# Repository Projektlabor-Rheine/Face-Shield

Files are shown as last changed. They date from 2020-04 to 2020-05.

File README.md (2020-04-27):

# Projektlabor Rheine face shield

This is the Repository of the face shield developed and produced by the *Projektlabor Rheine*.
Feel free to download and cut theese on your own Laser cutter. <br>
**We would be pleased to be named as authors in case of further use.**
**Please do not use in any commercial applications** <br>
The face shield is not a complete protection against the SARS-CoV-2 virus. However, it reduces the risk of infection. <br>
The system is not certified.

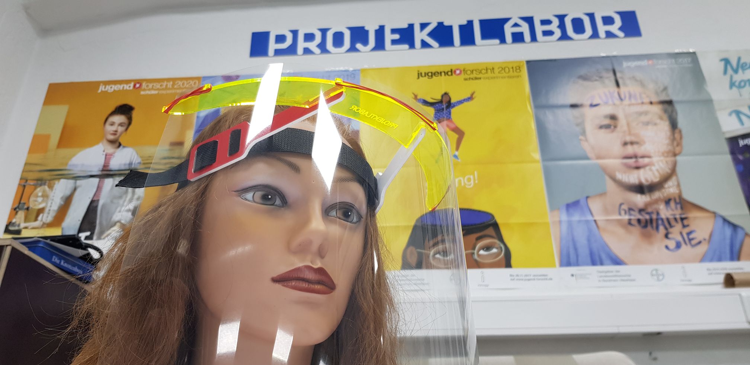
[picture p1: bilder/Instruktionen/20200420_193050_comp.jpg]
Faceshield


## Interested?
**Write to sommer@pkr-projekt.de**

## Ideas?
### Post on Instagram: @projektlabor or #plshield

## Making the Face shields:
- *Cutout's*:
   - Banana
   - Connector x2
- Velcro strap (25cm) soft
- Velcro strap (10cm) rough
- Textile Rubber belt 45cm
- Film/foil A4
- Rubber band x3
- Some Plastic Glue

#### Alternatively you can also build a shield with just the Velcro straps. For instructions on building these look [here](./Klettshields.md)

**Building the Face shields with a Rubber belt:**

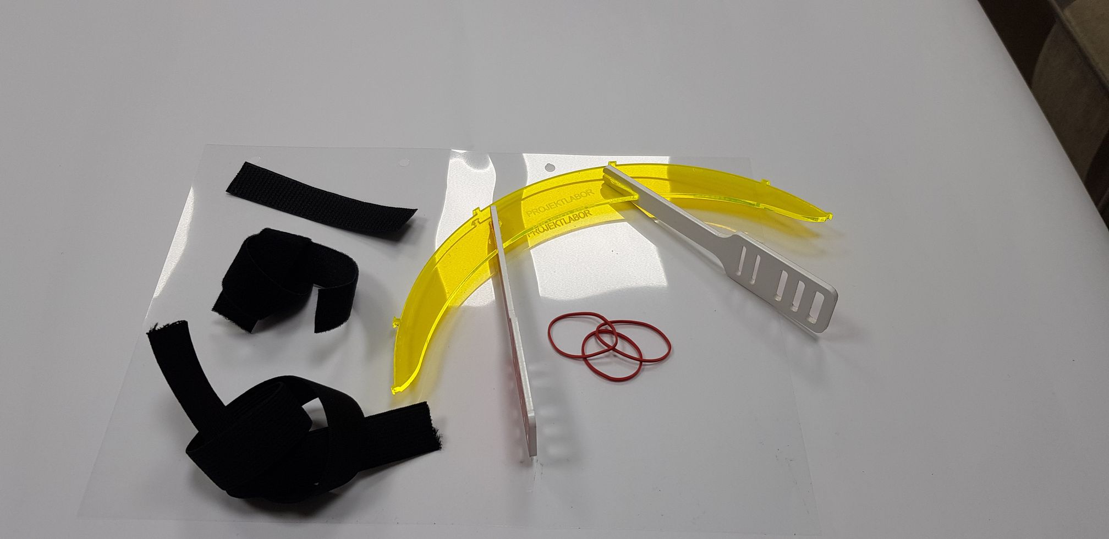
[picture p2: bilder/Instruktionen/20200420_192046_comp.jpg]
Material

Material you need to build the shields

### Building Instructions:

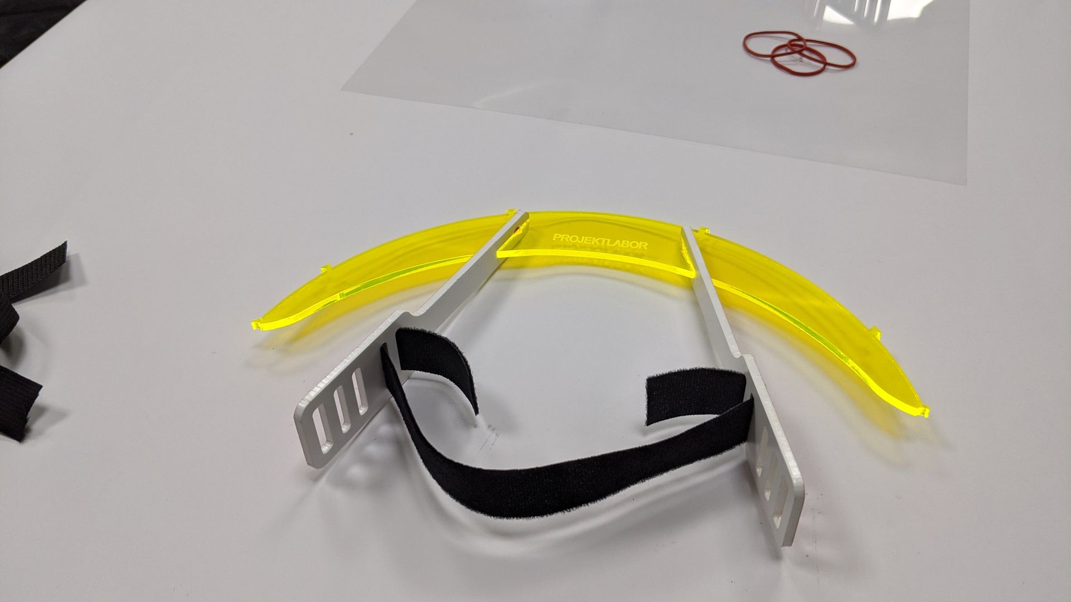
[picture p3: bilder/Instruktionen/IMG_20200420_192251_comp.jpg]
Velcro strap

Thread soft Velcro strap into both sides of the shield frame like shown above.

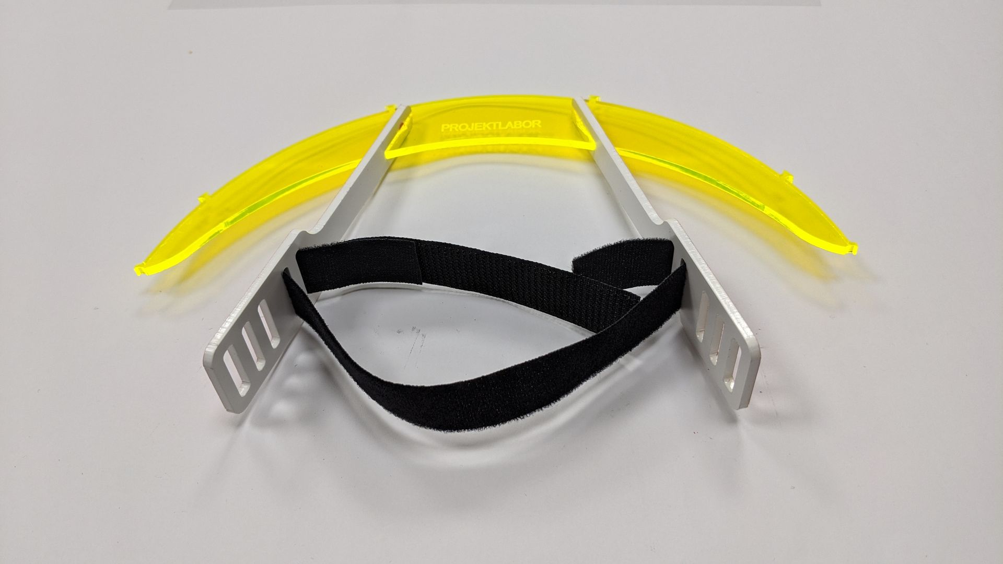
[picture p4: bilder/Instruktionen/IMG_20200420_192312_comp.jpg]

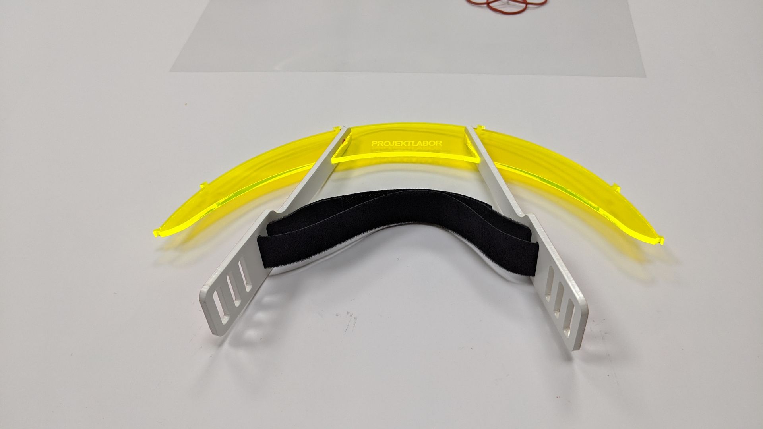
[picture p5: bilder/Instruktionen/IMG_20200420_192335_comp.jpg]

Use the rough type of Velcro strap to connect both sides

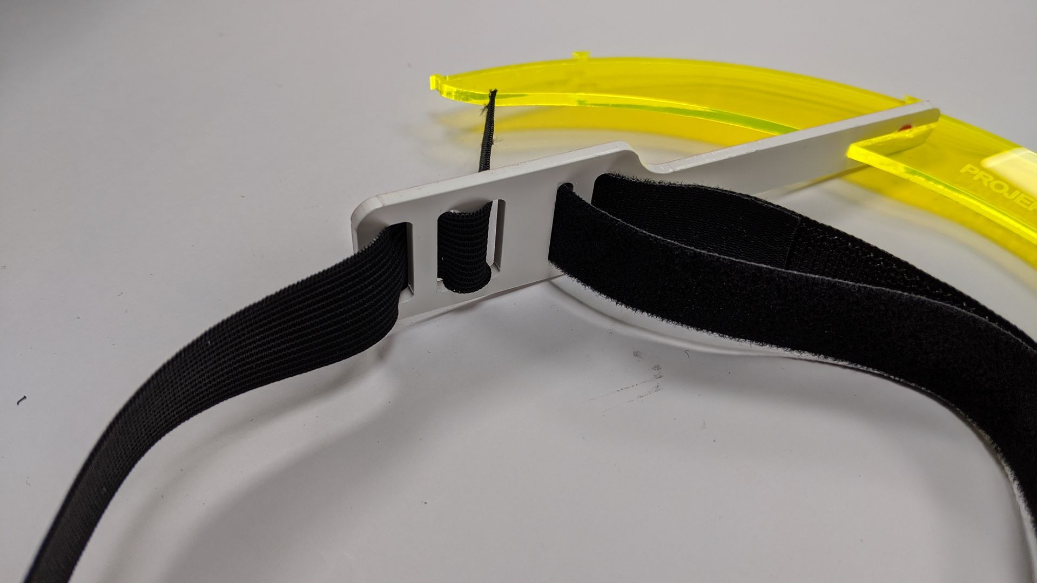
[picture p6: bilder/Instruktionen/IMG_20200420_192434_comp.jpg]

Now thread in the Textile Rubber belt like shown above.

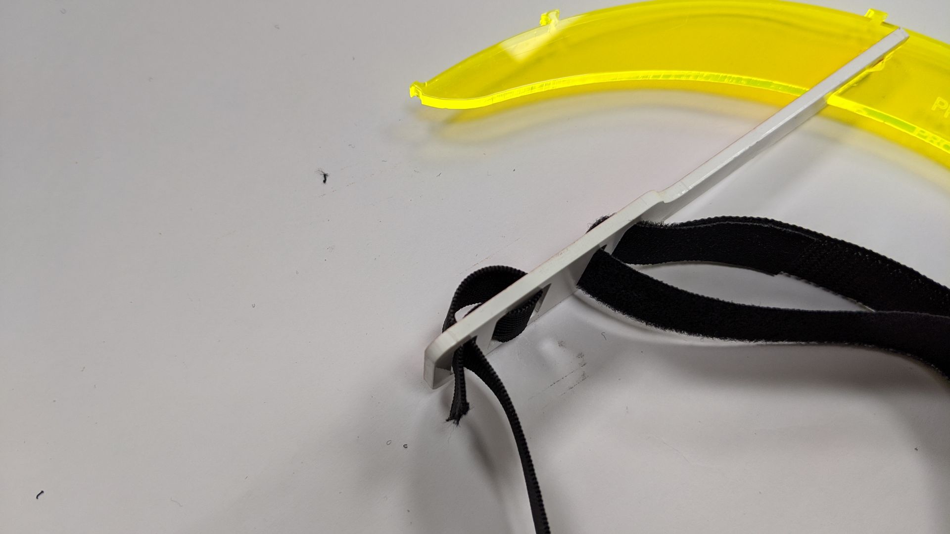
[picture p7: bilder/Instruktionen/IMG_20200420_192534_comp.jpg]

And back again to keep the belt from getting out of the frame. :)

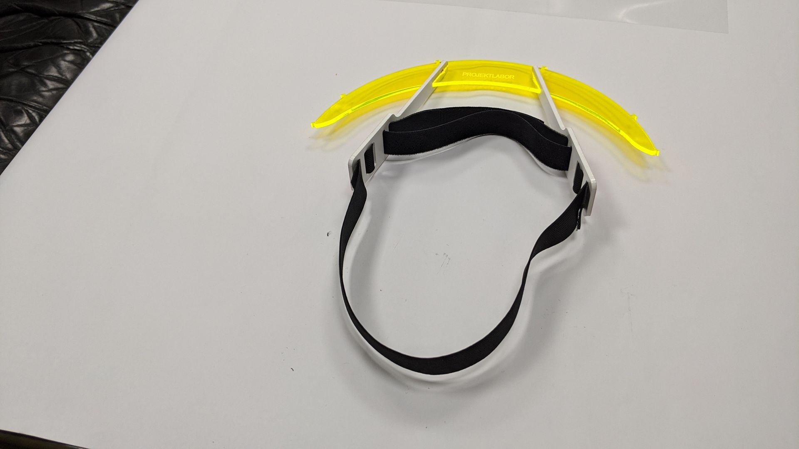
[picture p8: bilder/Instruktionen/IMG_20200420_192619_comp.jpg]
Almost done

Now on the other side aswell. Almost done!

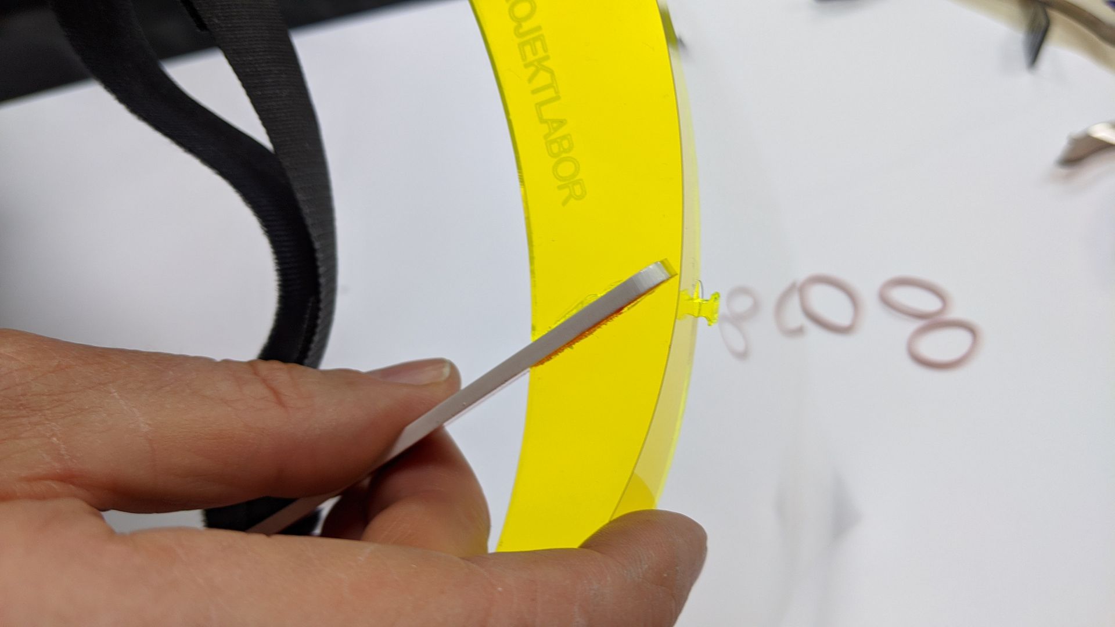
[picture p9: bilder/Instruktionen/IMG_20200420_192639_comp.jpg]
Foil installation

Punch 4Holes into the A4 film and put them onto the frame. 

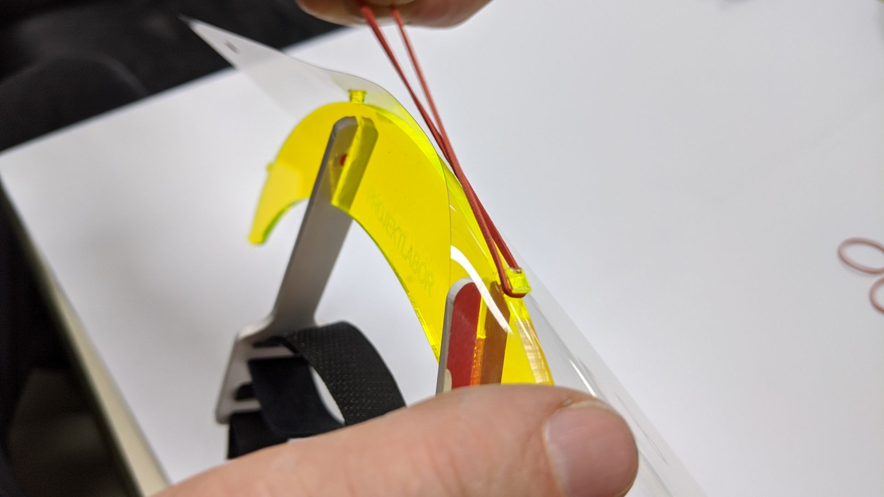
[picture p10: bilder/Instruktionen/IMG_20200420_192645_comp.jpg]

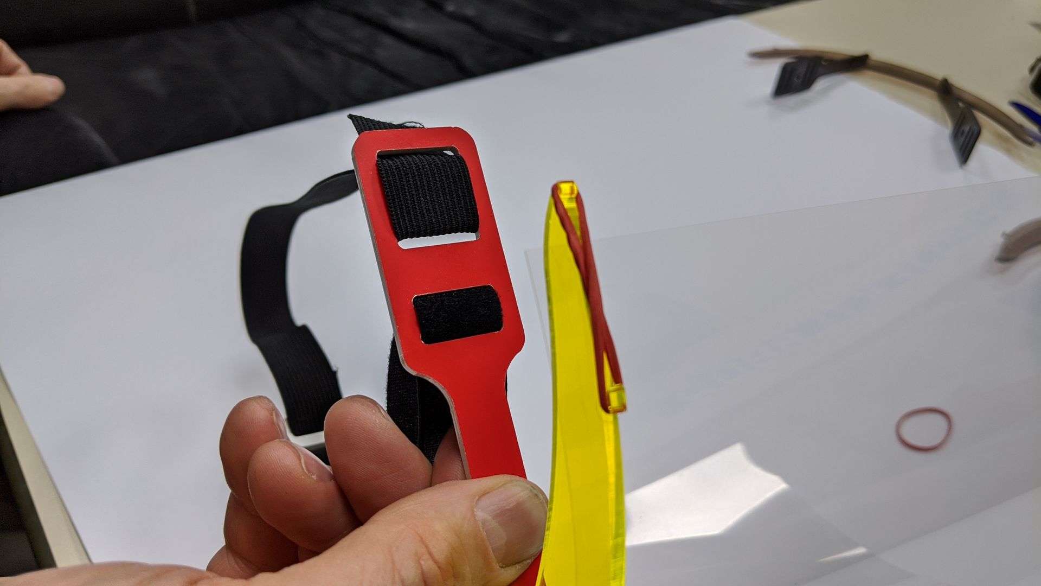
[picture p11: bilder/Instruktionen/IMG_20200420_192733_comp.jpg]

Use Rubber bands to secure the film in place

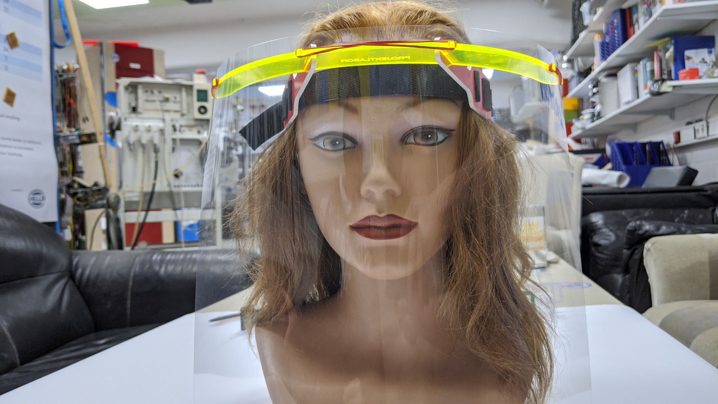
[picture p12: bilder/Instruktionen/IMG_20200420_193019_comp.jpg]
Done

**DONE !!!**

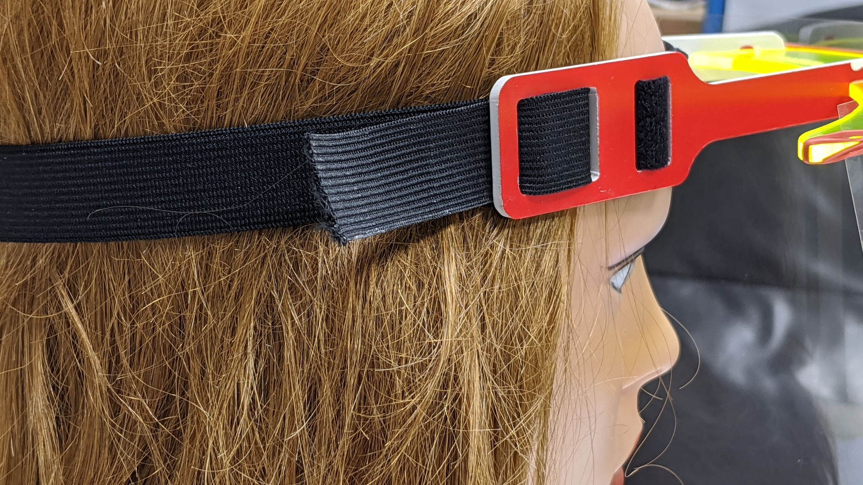
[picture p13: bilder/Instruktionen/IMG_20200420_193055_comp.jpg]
Tighten

You *can* tighten the Rubber!

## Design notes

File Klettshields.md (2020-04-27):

## Building Instructions for shields using Velcrostraps
The shield that uses just velcro straps has the advantage of being a little bit cheaper and It maybe easier to get material for.

### Material you need:

- Everything you needed for the other thing except the rubber belt
- Velcro strap soft
- Velcro strap rough

### Image instructions

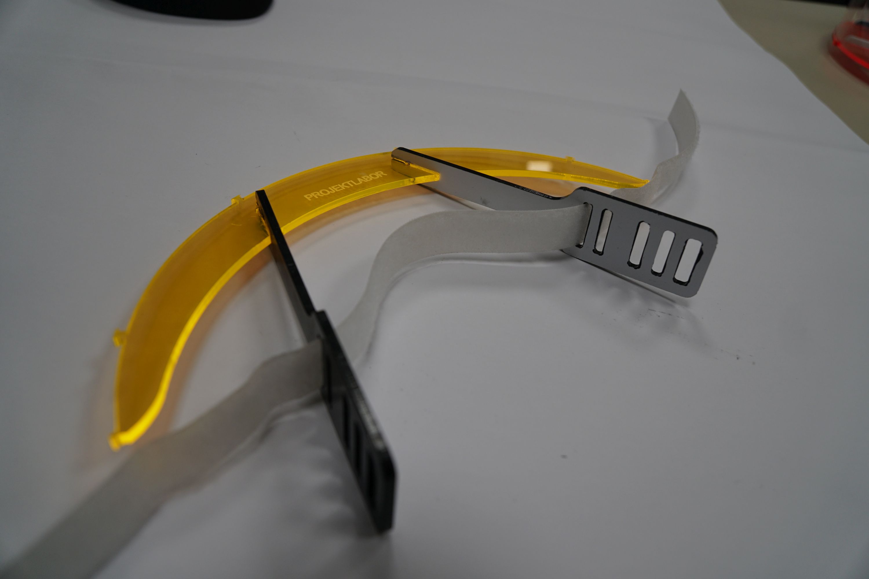
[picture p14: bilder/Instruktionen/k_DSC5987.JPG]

Insert the Velcrostrap into the first hole.

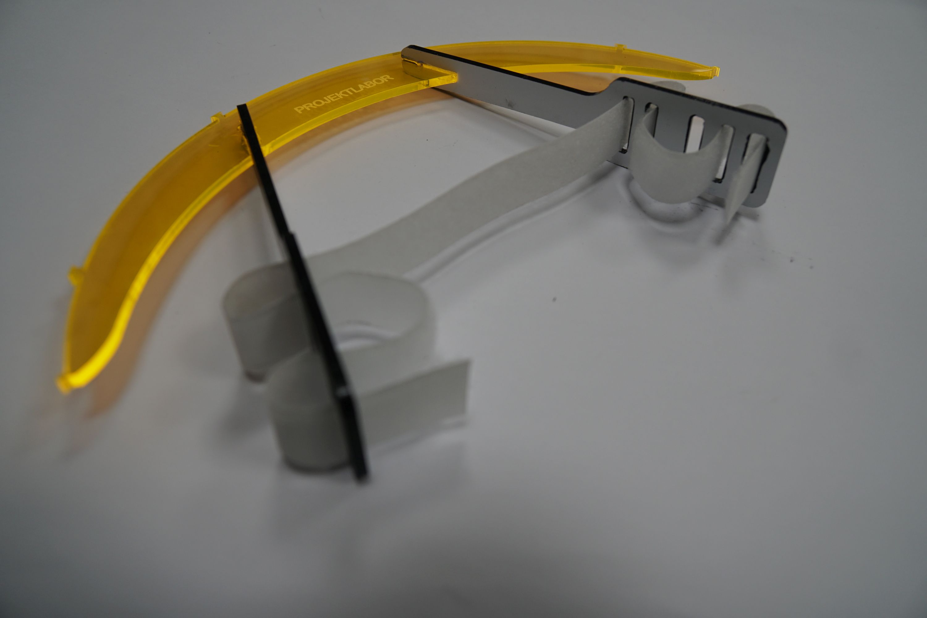
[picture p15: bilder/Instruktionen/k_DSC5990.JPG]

Thread it back into the second, out of the fourth and through the fifth back in again.

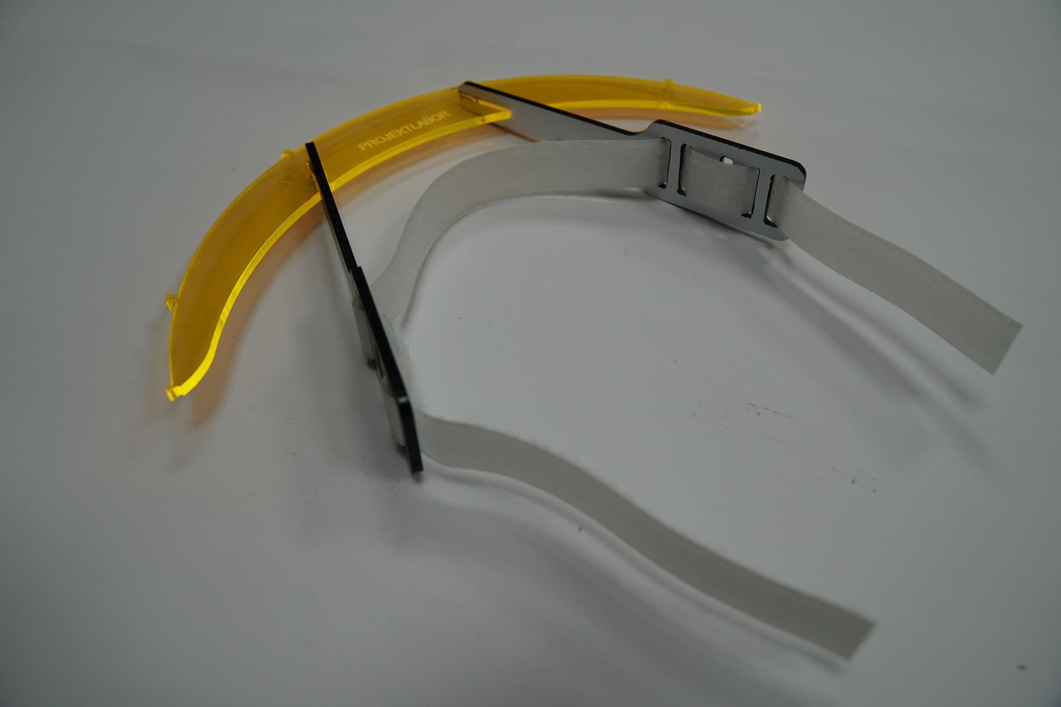
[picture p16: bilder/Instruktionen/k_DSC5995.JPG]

After that it looks like this.

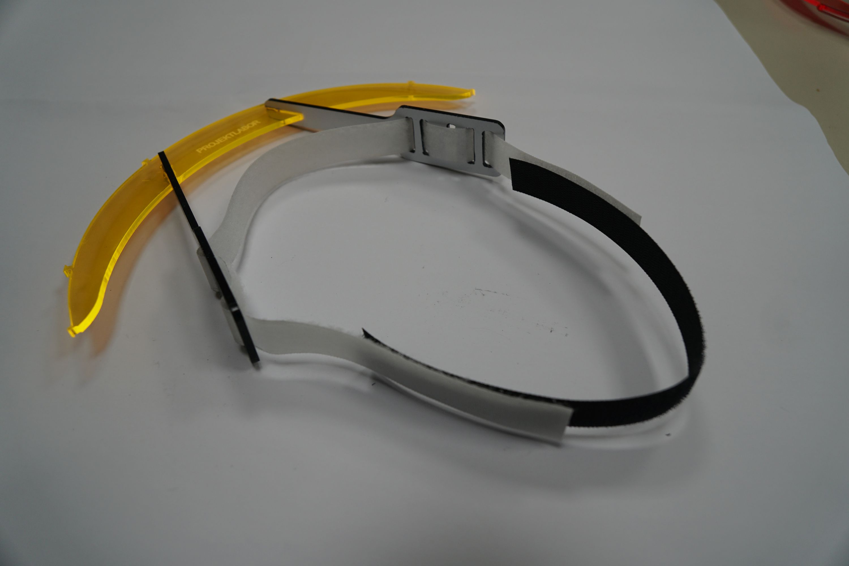
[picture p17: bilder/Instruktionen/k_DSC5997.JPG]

Then just add the other Velcrostrap and voila: Done!

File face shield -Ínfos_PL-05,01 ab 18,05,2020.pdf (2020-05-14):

## face shield PL – 05.01 ab 18.05.2020

Das System darf ausschließlich für nicht kommerzielle Zwecke kopiert, verändert und weiter entwickelt werden.

Bei jeder Nutzung ist der Urheber, Projektlabor Berufskolleg Rheine, zu nennen.

Das face shield aus dem Projektlabor wurde von Sven Hübner (G2M) und Jonas Huilmann (G1E) (begleitet von Christian Hoof und Berthold Sommer) entwickelt.
Alle planerischen und vorbereitenden Arbeiten wurden online durchgeführt.

Ziele des Projektes ist es ein face shild zu entwickeln (und später zu produzieren), das schnell, preiswert und auch in größeren Stückzahlen gefertigt werden kann.
Anforderungen an das System:
einfache Handhabbarkeit, hoher Tragekomfort, robuster alltagstauglicher
Aufbau, leicht zu reinigen, kurze Produktionszeiten, preisgünstige Herstellung (Materialien, Aufwand, Abläufe, …).

Acrylglas und Laseracryl
Drei Platten, die mit dem Lasercutter zugeschnitten werden, bilden das Grundgerüst.
Ein Zuschnitt aus 3 mm Acrylglas (oberes Schild). Hier wird die Schutzfolie befestigt.
Zwei Zuschnitte aus 3 mm Laseracryl. Sie bilden die Halter, für das obere
Schild. Das Laseracryl (wird z.B. für Beschriftungsschilder verwendet), ist

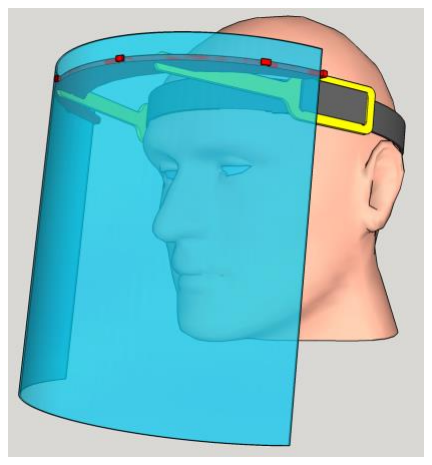
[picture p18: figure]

flexibler als das Acrylglas. Das System passt sich damit leicht an verschiedene Kopfformen an und die Entfernung zum Gesicht kann variiert werden.
Die mit dem Laser geschnittenen Platten werden zusammengesteckt. Um die Verbindung zu fixieren werden sie zusätzlich mit einem Spezialkleber verklebt.
Die glatten Oberflächen der Platten können leicht mit Seifenlauge gereinigt werden.

Klettband (20 mm breit)
Der face shield wird mit einem Klettband am Kopf befestigt. Dieses ermöglicht eine einfache Anpassung an verschiedene Kopfgrößen und -formen. Um einen hohen Tragekomfort zu erhalten, wird die weiche Seite nach innen gelegt. Die Klettbänder können einfach ausgetauscht und gewaschen werden.

Textilgummi (20 mm breit)
In einer überarbeiteten Version kann das face shield alternativ auch mit einem Textilgummiband am Kopf gehalten werden. Hierfür wurden die Löcher in den Seitenhaltern modifiziert. Die Bilder in diesem Dokument zeigen die ältere Version. Weitere Infos sind auf GitHub zu finden (Link s. u.)

Schutzfolie
Auf speziell anfertigte Folien haben wir bewusst verzichtet. Zum Einsatz kommt eine einfache A4 Folie, wie sie z.B. für den guten alten Overheadprojektor benötigt wird. Diese Folien können im Schreibwaren- oder Bürobedarf besorgt werden. Die Lochung ist eine 888er Lochung (Erweiterung der ISO-838-Lochung). Diese lässt sich mit einem handelsüblichen Locher, (Bürobedarf) sehr einfach herstellen. Die Folie kann mit Seifenlauge gereinigt werden. Verschlissene oder verknickte Folien sind leicht austauschbar.

Gummibänder
Die Schutzfolie wird auf kleine Stifte an dem oberen Schild gesteckt. Zum Fixieren werden einfache Gummibänder (Haushaltsbedarf) eingehängt.

Gesamtmasse (Acrylplatten, Klettband, Folie, Befestigungsgummis) 49 g

Alle Bauteile des Systems können mit Seifenlauge gereinigt werden.

Ein 40 W Lasercutter benötigt für 25 face shields etwa 74 Minuten zum Schneiden der
Platten. Die Bestückungszeit der Maschine beträgt etwa 2 Minuten.

Ein Dank geht an Eric Frey (G2E) und Jascha Wallmeyer (G1E), die unterstützend mitgeholfen haben.

Infos: https://github.com/Projektlabor-Rheine/Face-Shield

## face shield PL

–

0

### 5.01 ab 18.05.2020

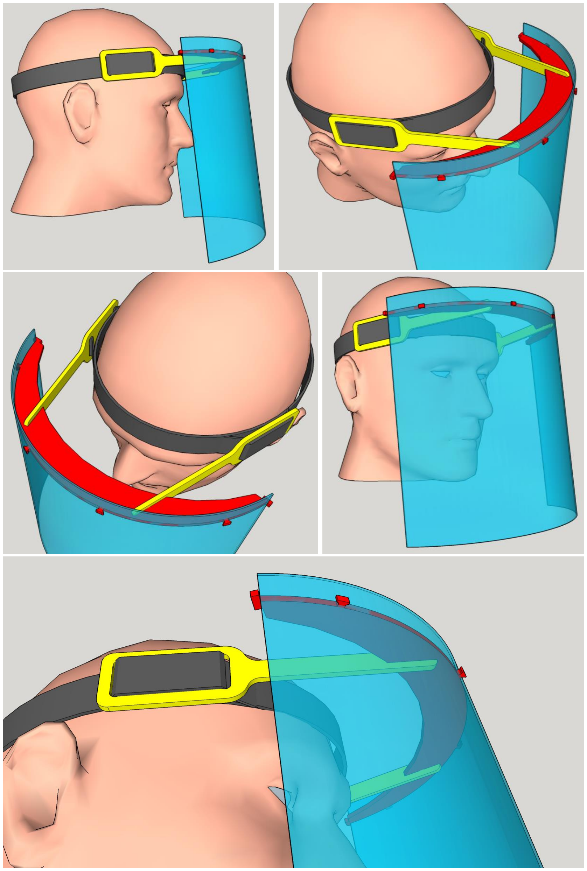
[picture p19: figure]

Seite

Das System darf ausschließlich für nicht kommerzielle Zwecke kopiert, verändert und weiter entwickelt werden.

Bei jeder Nutzung ist der Urheber, Projektlabor Berufskolleg Rheine, zu nennen.

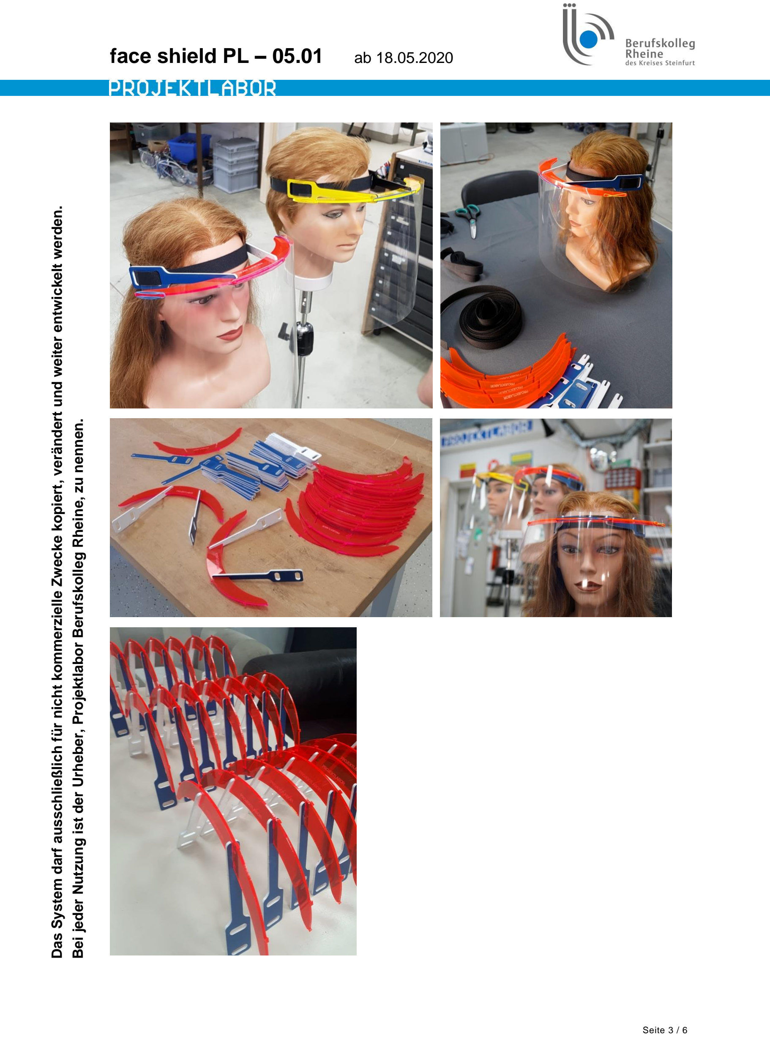
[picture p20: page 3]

Das System darf ausschließlich für nicht kommerzielle Zwecke kopiert, verändert und weiter entwickelt werden.

Bei jeder Nutzung ist der Urheber, Projektlabor Berufskolleg Rheine, zu nennen.

Das System darf ausschließlich für nicht kommerzielle Zwecke kopiert, verändert und weiter entwickelt werden.

Bei jeder Nutzung ist der Urheber, Projektlabor Berufskolleg Rheine, zu nennen.

Über Rückmeldungen und Verbesserungsvorschläge freuen wir uns.
In der Version 5.1 wurden (aufgrund der Rückmeldungen) folgende Änderungen vorgenommen:
1. Den Abstand zwischen Nase und Schutzfolie haben wir etwas verkleinert.
- Für Brillenträger, ist der Abstand immer noch groß genug. Auch ein Beschlagen der shields oder einer Brille wurde mit dem kürzeren Abstand nicht beobachtet. (Bei Bedarf z.B. für Arbeiten mit einer Lupenbrille können wir relativ einfach auch shields mit einem extra großen Abstand fertigen.)
2. Die Verbindung zwischen Halteband und Halter haben wir modifiziert. Das face shield kann nun (wie in den ersten Versionen) nur mit einem Klettband oder alternativ mit einem Gummizug am Kopf befestigt werden. Weiterhin kann bei beiden Versionen eine Anpassung an die individuelle Kopfform und –größe einfach vorgenommen werden:
- Bei der Version mit dem Klettband durch verschieben des Halters auf dem Klettband und entsprechendes Festkletten des Klettbandes. Das Tragen ist ähnlich wie bei einer Schirmmütze – ist diese einmal eingestellt, passt sie immer gleich.
- Bei der Version mit dem Gummiband ist das Kopfband geteilt. Das vordere Band ist eine Klettbandkombination und kann passend für die jeweilige Stirn eingestellt werden. Das hintere Band ist ein 20 mm breites Textilgummi, dies soll das Auf- und Absetzen für Menschen mit Pferdeschwanzfrisur erleichtern. Naturgemäß übt ein Gummizug aber einen leichten Druck auf den Kopf aus. Auch die Länge des Gummis kann am Halter individuell eingestellt werden.
3. Im oberen Halter wurde die Nut zur Aufnahme der seitlichen Halter um 5 mm verkürzt. Der verbliebende Acrylglassteg ist jetzt stabiler.

Infos zum Bezug der PL face shields

Leider ist der manuelle Aufwand für das Fertigen der Halter doch höher als ursprünglich angenommen, da die Teile aus dem Lasercutter vor dem zusammensetzten manuell nachbearbeitet werden müssen. Unsere Materialkosten liegen bei knapp 2,- € pro face shield. Aufgrund er vielen Anfragen ist der Aufwand für die Schüler nicht mehr leistbar. Deshalb haben wir unsere Teilzeitkräfte in den Produktionsablauf eingearbeitet, hier entstehen aber weiter Lohnkosten. Des Weiteren soll die Arbeit des Projektlabors https://projektlabor.org eine kleine Unterstützung erhalten. Den Preis haben wir deshalb um einen Euro erhöht.
Die face shields geben wir für 6,- € zzgl. Ust. als Bausatz mit allen notwendigen Materialien ab. Die Acrylhalter sind fertig geschnitten, zusammengesetzt und geklebt, die Folien sind passend gelocht. Sie müssen nur noch die Klett- bzw. Gummibänder einfädeln und die Folien einhängen.
Es wird also kein Werkzeug für den Zusammenbau benötigt.
Eine Anleitung mit vielen Bildern finden sie auf GitHub https://github.com/Projektlabor-Rheine/Face-Shield/blob/master/README.mdhttps://github.com/Projektlabor-Rheine/Face-Shield/blob/master/Klettshields.md

Eine Rechnungsstellung erfolgt über die Schülerfirma „Bücherkarussel" unseres Fördervereins. Sie bekommen also eine korrekte Rechnung für ihre Buchhaltung, die Umsatzsteuer wird für alle face shields ordnungsgemäß abgeführt. Für eine Bestellung geben sie bitte die Rechnungsadresse, Menge, Version (nur Klettband oder mit Textilgummi) angeben. Die face shields können sie dann nach Verabredung bei uns abholen. Ein Versand der face shields wäre gegebenenfalls möglich. Dies ist für uns aber mit einem sehr hohen Aufwand verbunden. Wir haben keine professionelle Verpackungsabteilung, es müssen passende Kartons organisiert, die Materiealien vernünftig einpackt, die Pakete adressiert, frankiert und zum Versand gebracht werden. Die Kosten (12,- € / Paket) würden wir nach Aufwand zusätzlich in Rechnung stellen. faceshield@projektlabor.org

Das System darf ausschließlich für nicht kommerzielle Zwecke kopiert, verändert und weiter entwickelt werden.

Bei jeder Nutzung ist der Urheber, Projektlabor Berufskolleg Rheine, zu nennen.

Weitere Infos zum Projekt haben wir auf GitHub veröffentlicht: https://github.com/Projektlabor-Rheine/Face-Shield
Neben den Hinweise zum Zusammenbau der face shields (einfädeln der Klett- bzw. Textilgummibänder und einhängen der Folien) finden Maker, die sich die Konstruktion nachbauen möchten, dort ebenfalls Infos. Mit einem ausreichenden handwerklichen Geschick, müsste dass sogar mit einer Dekupier- oder Laubsäge gehen (das ist dann allerdings wesentlich aufwändiger als mit dem Lasercutter).

Rückfragen, Anregungen und Verbesserungsvorschläge an: faceshield@projektlabor.org

Ein face shield, eine Mund-Nasen-Maske (ob selbstgenäht oder industriell gefertigt), ein Schal vor dem Gesicht, oder ähnliches ist kein Schutz vor einer eigenen Infektion. Sie dienen hauptsächlich zum Schutz anderer Menschen. Das funktioniert aber nur, wenn sie richtig getragen werden - achten sie also auf den korrekten Sitz ihrer Schutzaccessoires.
Zum Schutz vor einer Covid-19 Infektion gilt grundsätzlich:
Halten sie Abstand und beachten sie die Hygieneregeln.

Die geltenden Verordnungen unterliegen einem stetigen Wandel und sind je nach Region unterschiedlich. Informieren sie sich über die jeweils für sie geltenden Regeln.

Makingbegeisterte Grüße und bleiben Sie fit! Berthold Sommer

P.S.: Die Corona-Krise hat auch positive Effekte. An sehr vielen Orten sind Maker*innen aktiv, die viele kreative Ideen umsetzen, sich vernetzen und Dinge machen. Viel tausend Menschen die mit ihren Nähmaschinen Schutzmasken nähen, Leute mit 3D-Druckern Ventile für Atemgeräte und ebenfalls Halter für face shields herstellen, kreative Bastler die sich coole Dinge überlegen um Menschen zu helfen, die meisten nutzen das Netz für Informationen und einen synergetischen Austausch, Andere organisieren in den sozialen Netzen Hilfe für Bedürftige, ….
Wir würden uns freuen, wenn wir viel von diesem kreativen Miteinander auch für die Zeit nach der Krise bewahren können.

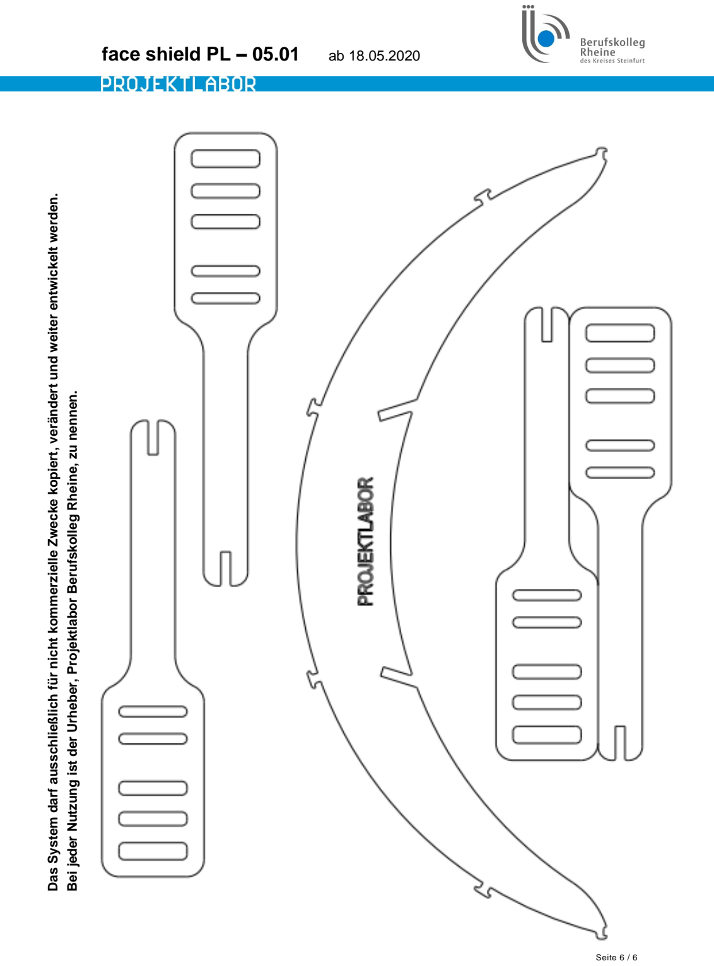
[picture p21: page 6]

Das System darf ausschließlich für nicht kommerzielle Zwecke kopiert, verändert und weiter entwickelt werden.

Bei jeder Nutzung ist der Urheber, Projektlabor Berufskolleg Rheine, zu nennen.

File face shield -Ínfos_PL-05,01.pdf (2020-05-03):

## face shield PL – 05.01

Das System darf ausschließlich für nicht kommerzielle Zwecke kopiert, verändert und weiter entwickelt werden.

Bei jeder Nutzung ist der Urheber, Projektlabor Berufskolleg Rheine, zu nennen.

Das face shield aus dem Projektlabor wurde von Sven Hübner (G2M) und Jonas Huilmann (G1E) (begleitet von Christian Hoof und Berthold Sommer) entwickelt.
Alle planerischen und vorbereitenden Arbeiten wurden online durchgeführt.

Ziele des Projektes ist es ein face shild zu entwickeln (und später zu produzieren), das schnell, preiswert und auch in größeren Stückzahlen gefertigt werden kann.
Anforderungen an das System:
einfache Handhabbarkeit, hoher Tragekomfort, robuster alltagstauglicher
Aufbau, leicht zu reinigen, kurze Produktionszeiten, preisgünstige Herstellung (Materialien, Aufwand, Abläufe, …).

Acrylglas und Laseracryl
Drei Platten, die mit dem Lasercutter zugeschnitten werden, bilden das Grundgerüst.
Ein Zuschnitt aus 3 mm Acrylglas (oberes Schild). Hier wird die Schutzfolie befestigt.
Zwei Zuschnitte aus 3 mm Laseracryl. Sie bilden die Halter, für das obere
Schild. Das Laseracryl (wird z.B. für Beschriftungsschilder verwendet), ist


flexibler als das Acrylglas. Das System passt sich damit leicht an verschiedene Kopfformen an und die Entfernung zum Gesicht kann variiert werden.
Die mit dem Laser geschnittenen Platten werden zusammengesteckt. Um die Verbindung zu fixieren werden sie zusätzlich mit einem Spezialkleber verklebt.
Die glatten Oberflächen der Platten können leicht mit Seifenlauge gereinigt werden.

Klettband (20 mm breit)
Der face shield wird mit einem Klettband am Kopf befestigt. Dieses ermöglicht eine einfache Anpassung an verschiedene Kopfgrößen und -formen. Um einen hohen Tragekomfort zu erhalten, wird die weiche Seite nach innen gelegt. Die Klettbänder können einfach ausgetauscht und gewaschen werden.

Textilgummi (20 mm breit)
In einer überarbeiteten Version kann das face shield alternativ auch mit einem Textilgummiband am Kopf gehalten werden. Hierfür wurden die Löcher in den Seitenhaltern modifiziert. Die Bilder in diesem Dokument zeigen die ältere Version. Weitere Infos sind auf GitHub zu finden (Link s. u.)

Schutzfolie
Auf speziell anfertigte Folien haben wir bewusst verzichtet. Zum Einsatz kommt eine einfache A4 Folie, wie sie z.B. für den guten alten Overheadprojektor benötigt wird. Diese Folien können im Schreibwaren- oder Bürobedarf besorgt werden. Die Lochung ist eine 888er Lochung (Erweiterung der ISO-838-Lochung). Diese lässt sich mit einem handelsüblichen Locher, (Bürobedarf) sehr einfach herstellen. Die Folie kann mit Seifenlauge gereinigt werden. Verschlissene oder verknickte Folien sind leicht austauschbar.

Gummibänder
Die Schutzfolie wird auf kleine Stifte an dem oberen Schild gesteckt. Zum Fixieren werden einfache Gummibänder (Haushaltsbedarf) eingehängt.

Gesamtmasse (Acrylplatten, Klettband, Folie, Befestigungsgummis) 49 g

Alle Bauteile des Systems können mit Seifenlauge gereinigt werden.

Ein 40 W Lasercutter benötigt für 25 face shields etwa 74 Minuten zum Schneiden der
Platten. Die Bestückungszeit der Maschine beträgt etwa 2 Minuten.

Ein Dank geht an Eric Frey (G2E) und Jascha Wallmeyer (G1E), die unterstützend mitgeholfen haben.

Infos: https://github.com/Projektlabor-Rheine/Face-Shield

## face shield PL

–

0

5.01


Seite

/

Das System darf ausschließlich für nicht kommerzielle Zwecke kopiert, verändert und weiter entwickelt werden.

Bei jeder Nutzung ist der Urheber, Projektlabor Berufskolleg Rheine, zu nennen.

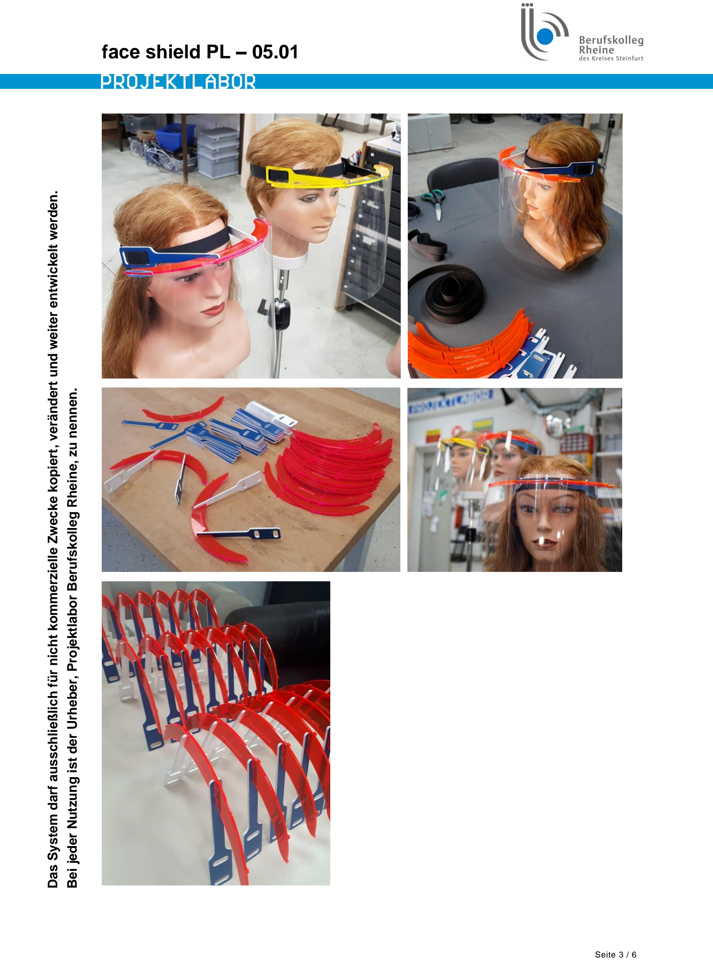
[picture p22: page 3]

Das System darf ausschließlich für nicht kommerzielle Zwecke kopiert, verändert und weiter entwickelt werden.

Bei jeder Nutzung ist der Urheber, Projektlabor Berufskolleg Rheine, zu nennen.

Das System darf ausschließlich für nicht kommerzielle Zwecke kopiert, verändert und weiter entwickelt werden.

Bei jeder Nutzung ist der Urheber, Projektlabor Berufskolleg Rheine, zu nennen.

Über Rückmeldungen und Verbesserungsvorschläge freuen wir uns.
In der Version 5.1 wurden (aufgrund der Rückmeldungen) folgende Änderungen vorgenommen:
1. Den Abstand zwischen Nase und Schutzfolie haben wir etwas verkleinert.
- Für Brillenträger, ist der Abstand immer noch groß genug. Auch ein Beschlagen der shields oder einer Brille wurde mit dem kürzeren Abstand nicht beobachtet.
(Bei Bedarf z.B. für Arbeiten mit einer Lupenbrille können wir relativ einfach auch shields mit einem extra großen Abstand fertigen.)
2. Die Verbindung zwischen Halteband und Halter haben wir modifiziert. Das face shield kann nun (wie in den ersten Versionen) nur mit einem Klettband oder alternativ mit einem Gummizug am Kopf befestigt werden. Weiterhin kann bei beiden Versionen eine Anpassung an die individuelle Kopfform und –größe einfach vorgenommen werden:
- Bei der Version mit dem Klettband durch verschieben des Halters auf dem Klettband und entsprechendes Festkletten des Klettbandes. Das Tragen ist ähnlich wie bei einer Schirmmütze – ist diese einmal eingestellt, passt sie immer gleich.
- Bei der Version mit dem Gummiband ist das Kopfband geteilt. Das vordere Band ist eine Klettbandkombination und kann passend für die jeweilige Stirn eingestellt werden. Das hintere Band ist ein 20 mm breites Textilgummi, dies soll das Auf- und Absetzen für Menschen mit Pferdeschwanzfrisur erleichtern. Naturgemäß übt ein Gummizug aber einen leichten Druck auf den Kopf aus. Auch die Länge des Gummis kann am Halter individuell eingestellt werden.
3. Im oberen Halter wurde die Nut zur Aufnahme der seitlichen Halter um 5 mm verkürzt. Der verbliebende Acrylglassteg ist jetzt stabiler.

Infos zum Bezug der PL face shields

Leider ist der manuelle Aufwand für das Fertigen der Halter doch höher als ursprünglich angenommen, da die Teile aus dem Lasercutter vor dem zusammensetzten manuell nachbearbeitet werden müssen. Unsere Materialkosten liegen bei knapp 2,- € pro face shield. Den Schülern, welche viel Engagement und Zeit in die Entwicklung investiert haben und jetzt engagiert mit der Produktion beschäftigt sind, soll eine Entlohnung für ihre Arbeit zukommen. Des Weiteren soll die Arbeit des Projektlabors https://projektlabor.org eine kleine Unterstützung erhalten.
Die face shields geben wir für 5,- € zzgl. Ust. als Bausatz mit allen notwendigen Materialien ab. Die Acrylhalter sind fertig geschnitten, zusammengesetzt und geklebt, die Folien ist passend gelocht. Sie müssen nur noch die Klett- bzw. Gummibänder einfädeln und die Folie einhängen.
Es wird also kein Werkzeug für den Zusammenbau benötigt.
Eine Anleitung mit vielen Bildern finden sie auf GitHub https://github.com/Projektlabor-Rheine/Face-Shield/blob/master/README.mdhttps://github.com/Projektlabor-Rheine/Face-Shield/blob/master/Klettshields.md

Eine Rechnungsstellung erfolgt über die Schülerfirma „Bücherkarussel" unseres Fördervereins. Sie bekommen also eine korrekte Rechnung für ihre Buchhaltung, die Umsatzsteuer wird für alle face shields ordnungsgemäß abgeführt. Für eine Bestellung geben sie bitte die Rechnungsadresse, Menge, Version (nur Klettband oder mit Textilgummi) angeben. Die face shields können sie dann nach Verabredung bei uns abholen. Ein Versand der face shields wäre gegebenenfalls möglich. Dies ist für uns aber mit einem sehr hohen Aufwand verbunden. Wir haben keine professionelle Verpackungsabteilung, es müssen passende Kartons organisiert, die Materiealien vernünftig einpackt, die Pakete adressiert, frankiert und zum Versand gebracht werden. Die Kosten würden wir nach Aufwand zusätzlich in Rechnung stellen. faceshield@projektlabor.org

Das System darf ausschließlich für nicht kommerzielle Zwecke kopiert, verändert und weiter entwickelt werden.

Bei jeder Nutzung ist der Urheber, Projektlabor Berufskolleg Rheine, zu nennen.

Weitere Infos zum Projekt haben wir auf GitHub veröffentlicht: https://github.com/Projektlabor-Rheine/Face-Shield
Neben den Hinweise zum Zusammenbau der face shields (einfädeln der Klett- bzw. Textilgummibänder und einhängen der Folien) finden Maker, die sich die Konstruktion nachbauen möchten, dort ebenfalls Infos. Mit einem ausreichenden handwerklichen Geschick, müsste dass sogar mit einer Dekupier- oder Laubsäge gehen (das ist dann allerdings wesentlich aufwändiger als mit dem Lasercutter).

Rückfragen, Anregungen und Verbesserungsvorschläge an: faceshield@projektlabor.org

Ein fache shield, eine Mund-Nasen-Maske (ob selbstgenäht oder industriell gefertigt), ein Schal vor dem Gesicht, oder ähnliches ist kein Schutz vor einer eigenen Infektion. Sie dienen hauptsächlich zum Schutz anderer Menschen. Das funktioniert aber nur, wenn sie richtig getragen werden - achten sie also auf den korrekten Sitz ihrer Schutzaccessoires.
Zum Schutz vor einer Covid-19 Infektion gilt grundsätzlich:
Halten sie Abstand und beachten sie die Hygieneregeln.

Die geltenden Verordnungen unterliegen einem stetigen Wandel und sind je nach Region unterschiedlich. Informieren sie sich über die jeweils für sie geltenden Regeln.

Makingbegeisterte Grüße und bleiben Sie fit! Berthold Sommer

P.S.: Die Corona-Krise hat auch positive Effekte. An sehr vielen Orten sind Maker*innen aktiv, die viele kreative Ideen umsetzen, sich vernetzen und Dinge machen. Viel tausend Menschen die mit ihren Nähmaschinen Schutzmasken nähen, Leute mit 3D-Druckern Ventile für Atemgeräte und ebenfalls Halter für face shields herstellen, kreative Bastler die sich coole Dinge überlegen um Menschen zu helfen, die meisten nutzen das Netz für Informationen und einen synergetischen Austausch, Andere organisieren in den sozialen Netzen Hilfe für Bedürftige, ….
Wir würden uns freuen, wenn wir viel von diesem kreativen Miteinander auch für die Zeit nach der Krise bewahren können.

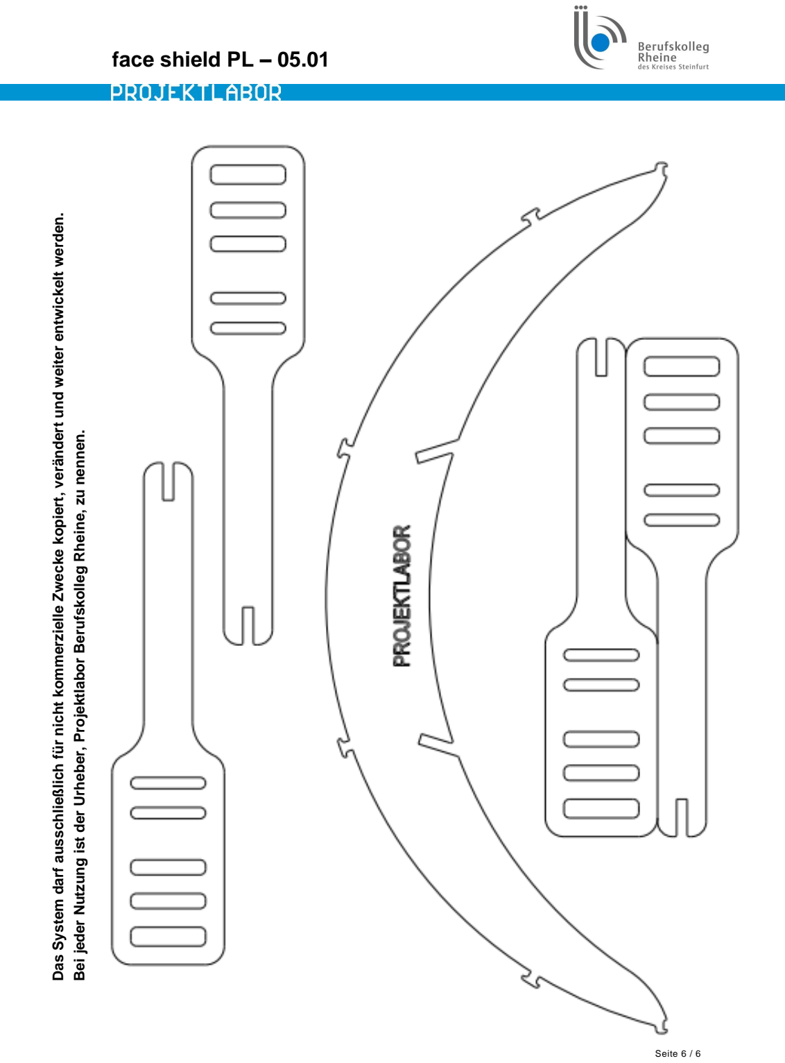
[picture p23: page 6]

Das System darf ausschließlich für nicht kommerzielle Zwecke kopiert, verändert und weiter entwickelt werden.

Bei jeder Nutzung ist der Urheber, Projektlabor Berufskolleg Rheine, zu nennen.

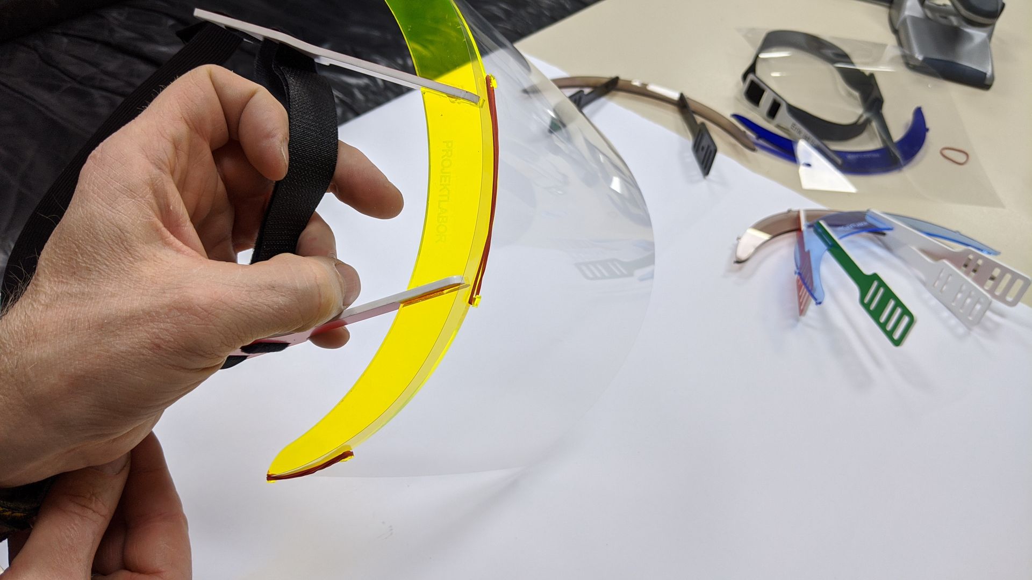
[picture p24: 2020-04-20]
bilder/Instruktionen/IMG_20200420_192853_comp.jpg

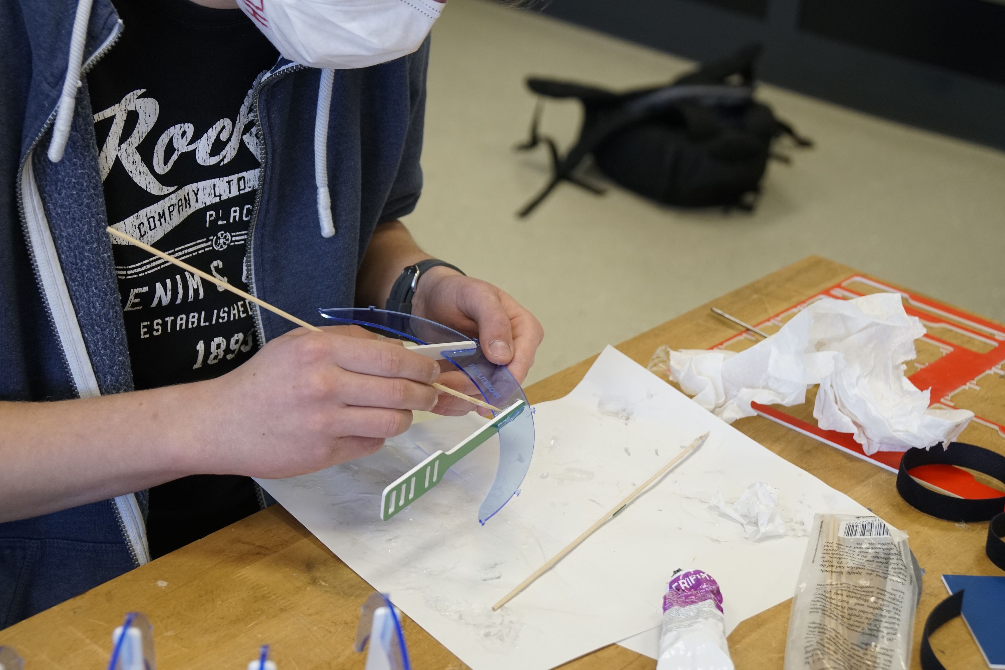
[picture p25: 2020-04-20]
bilder/_DSC5838_.jpg

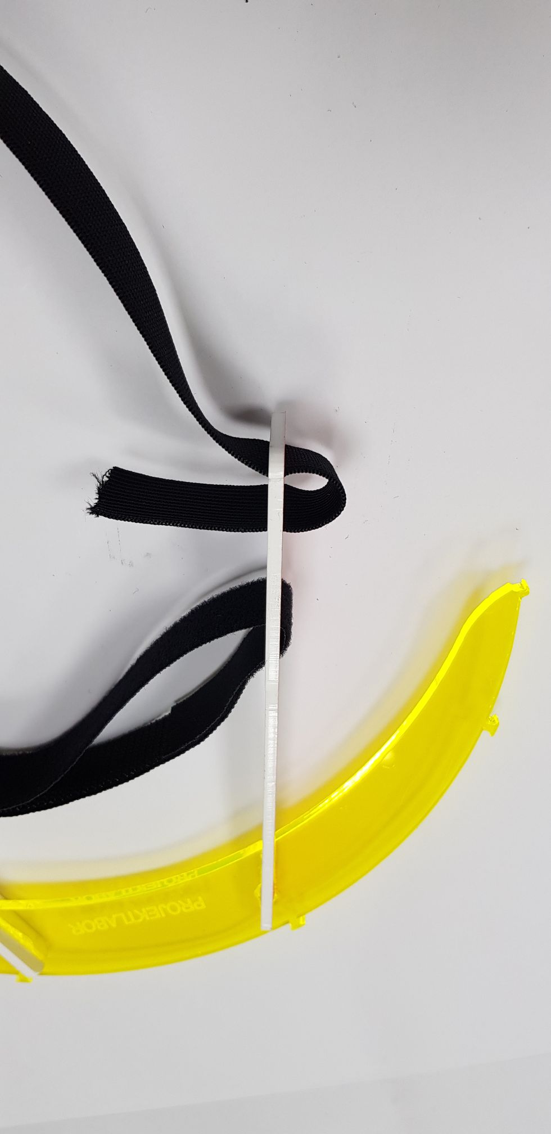
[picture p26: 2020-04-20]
bilder/Instruktionen/20200420_192414_comp.jpg

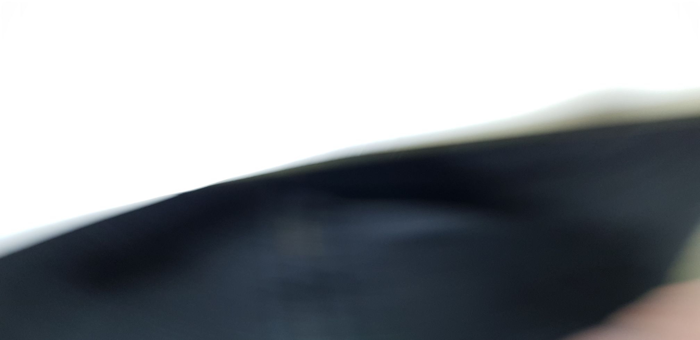
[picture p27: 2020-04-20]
bilder/Instruktionen/20200420_192244_comp.jpg

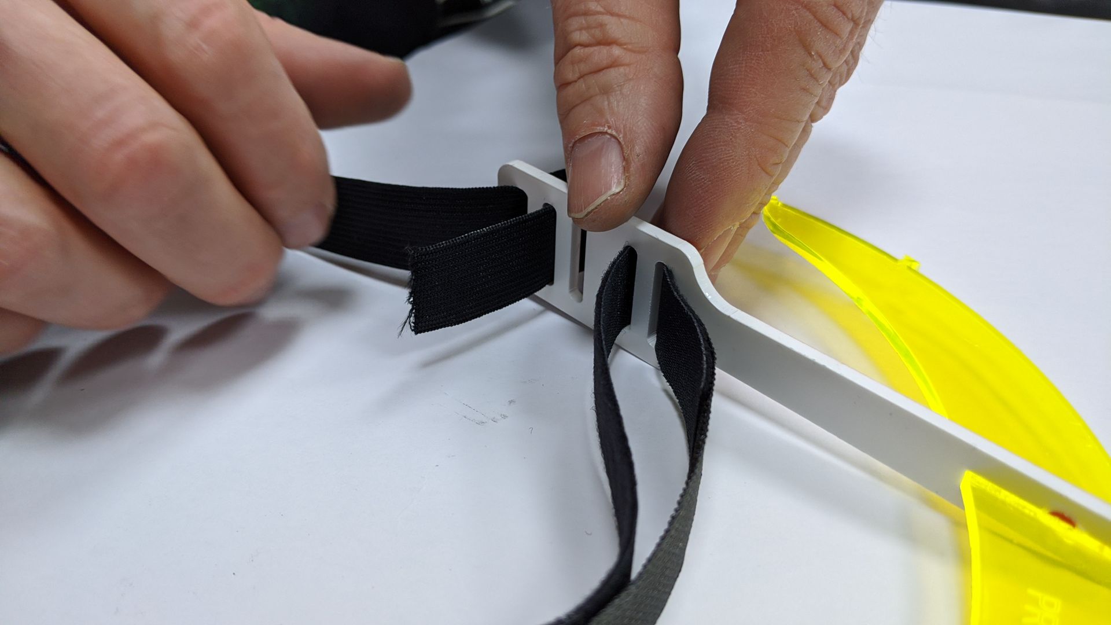
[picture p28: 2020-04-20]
bilder/Instruktionen/MVIMG_20200420_192404_comp.jpg

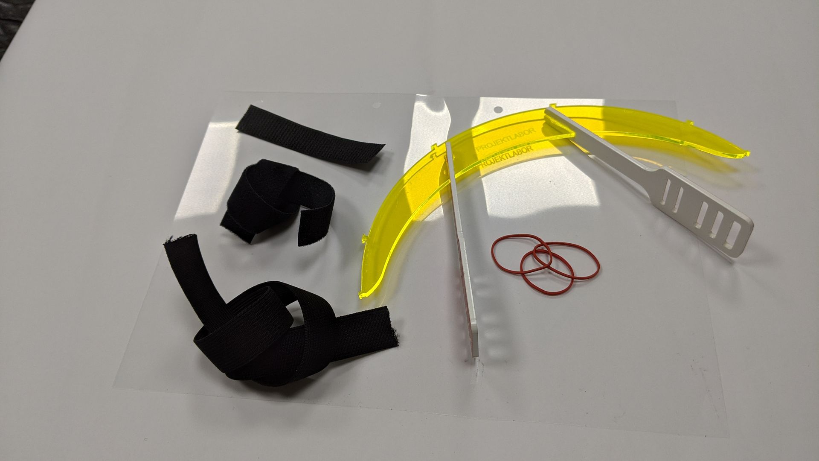
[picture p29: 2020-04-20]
bilder/Instruktionen/IMG_20200420_192106_comp.jpg

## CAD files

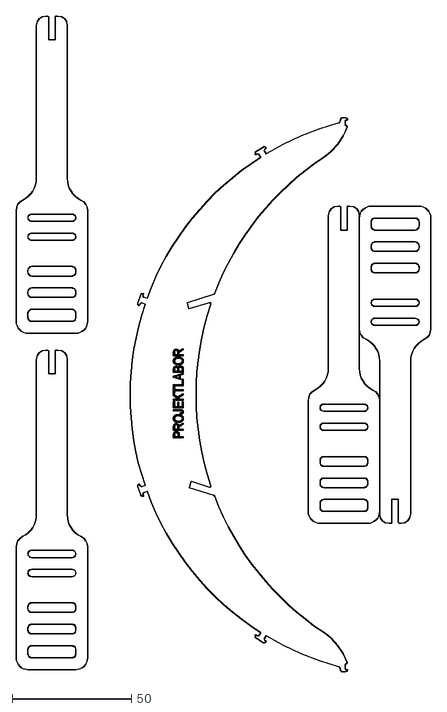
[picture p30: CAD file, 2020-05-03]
Face shield PL 05,01.dxf
174.0 x 275.0

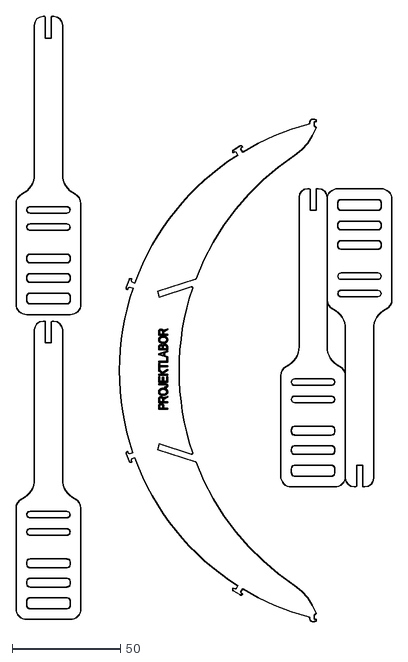
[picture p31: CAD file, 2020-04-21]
Face shield PL 05.dxf
174.0 x 280.0

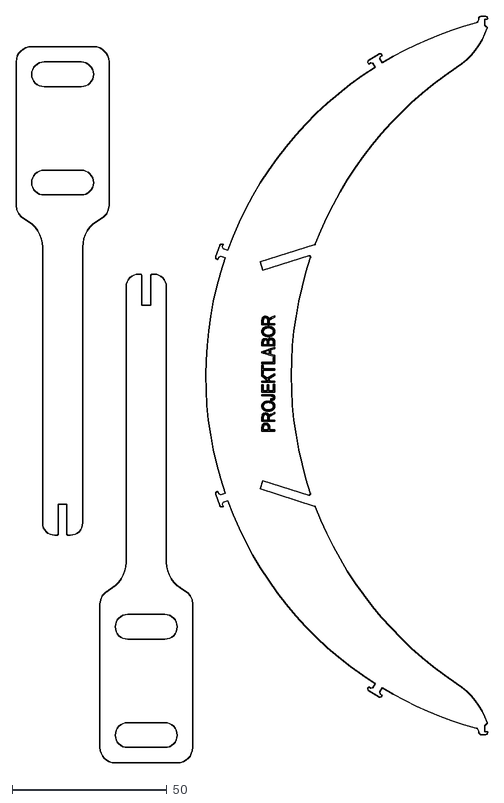
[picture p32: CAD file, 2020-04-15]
Face shield PL 03.dxf
152.5 x 241.5
